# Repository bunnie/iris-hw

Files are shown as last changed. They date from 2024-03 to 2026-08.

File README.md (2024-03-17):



# IRIS CAD files

This repository contains IRIS CAD files not found elsewhere.

In particular, the base machine is the [Jubilee3D](https://jubilee3d.com/index.php?title=Main_Page); please refer to its [github](https://github.com/machineagency/jubilee) for its base CAD files.

## About IRIS

This repository is part of the IRIS project, an effort to make it easier to verify the construction of silicon chips.

Read more about IRIS at our [arXiv paper](https://arxiv.org/abs/2303.07406), or the latest [project update](https://www.bunniestudios.com/blog/?p=6937).

## Acknowledgements

This work was funded in part by NLnet’s [NGI0 Entrust](https://nlnet.nl/entrust/) fund, established with support from the European Commission’s Next Generation Internet Program, and my [Github Sponsors](https://github.com/sponsors/bunnie/).

NLnet Logo

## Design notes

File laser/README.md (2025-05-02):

# Laser Mount

This is an experimental extension to the IRIS tool that adds a laser
to the illumination capabilities. The driver is designed to work with
a 1064nm Fabrey-Perot laser diode with a max power rating of 300mW,
such as the ThorLabs L1064H1.

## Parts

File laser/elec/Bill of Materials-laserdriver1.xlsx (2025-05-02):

Comment | Description | Designator | Footprint | LibRef | Quantity | MPN | VENDOR
22uF, 6.3V, X5R | Capacitor (Semiconductor SIM Model) | C1 | B_CAP0603 | Cap Semi | 1 | CL10A226KQ8NRNE | Samsung
10uF, 6.3V, X5R | Capacitor (Semiconductor SIM Model) | C2, C4, C5, C6 | B_CAP0603 | Cap Semi | 4 | CL10A106MQ8NNNC | Samsung
0.1uF, 25V, X7R | Capacitor (Semiconductor SIM Model) | C3 | B_CAP0402 | Cap Semi | 1 | CL05A104KA5NNNC | Samsung
L1064H1 | Typical RED, GREEN, YELLOW, AMBER GaAs LED | D1 | TO-CAN-MICROJACK | LED2 | 1 | L1064H1 | Thorlabs
white LED | Typical RED, GREEN, YELLOW, AMBER GaAs LED | D2 | B_LED0805 | LED2 | 1 | EAST2012WA1 | Everlight
red LED | Typical RED, GREEN, YELLOW, AMBER GaAs LED | D3 | B_LED0805 | LED2 | 1 | ANY | ANY
USB4085-GF-A_REVB | USB-C (USB TYPE-C) USB 2.0 Receptacle Connector 24 (16+8 Dummy) Position Through Hole, Right Angle, low cost, 3.46mm profile, 16 pin, horizontal, Top mount | J1 | GCT_USB4085-GF-A_REVB | USB4085-GF-A_REVB | 1 | USB4085-GF-A | GCT
2.2uH SRP3212-2R2M | Magnetic-Core Inductor | L1 | B_IND1210_BOURNES | Inductor Iron | 1 | SRP3212-2R2M | Bournes
0.47uH 0603 | Magnetic-Core Inductor | L2 | B_IND0603 | Inductor Iron | 1 | TFM160808ALC-R47MTAA | TDK
917-43-103-41-005000 | Placeholder for non-board BOM items | NT1 |  | NOTE | 1 | 917-43-103-41-005000 | Mil-Max
FH34SRJ-10S-0.5SH | Header, 10-Pin | P1, P2 | HRS_FH34SRJ-10S-0.5SH(50) | Header 10 | 2 | FH34SRJ-10S-0.5SH | Hirose
Header 6 | Header, 6-Pin | P3 | HDR1X6 | Header 6 | 1
DMG1012UW-7 | N-Channel MOSFET | Q1, Q2 | SOT323-3AN | MOSFET-N | 2 | DMG1012UW-7 | Diodes Inc
10k, 1% | Resistor | R1, R2 | B_RES0402 | Res1 | 2 | ANY | ANY
0.33 ohm 1% | Resistor | R3 | B_RES0603 | Res1 | 1 | ERJ-3BQFR33V | Panasonic
3.3k, 1% | Resistor | R4, R5 | B_RES0402 | Res1 | 2 | ANY | ANY
0 ohm | Resistor | R6 | B_RES0402 | Res1 | 1 | ANY | ANY
51, 1% | Resistor | R7 | B_RES0603 | Res1 | 1 | ANY | ANY
180, 1% | Resistor | R8 | B_RES0603 | Res1 | 1 | ANY | ANY
249k, 1%, +/-200ppm | Resistor | R9 | B_RES0402 | Res1 | 1 | RC0402FR-07249KL | Yageo
5.1k, 1% | Resistor | R10, R11 | B_RES0603 | Res1 | 2 | RC0603FR-075K1L | Yageo
TPS92001 | 1.5A high efficiency synchronous buck LED driver | U1 | TI-WSON65P200X80_HS-7N | TPS92201 | 1
TMP1075NDRLR | Temperature sensor, I2C | U2 | TI-SON50P200X80_HS-9N | TMP1075N | 1
TPS62802 | Buck regulator, 4MHz, 0.6A, 1.8V-3.3V, low Iq | U3 | BGA6C35P2X3_70X105X40_NSMD | TPS62802 | 1 | TPS62802YKAR | TI

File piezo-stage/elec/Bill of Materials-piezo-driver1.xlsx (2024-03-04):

Comment | Description | Designator | Footprint | LibRef | Quantity | VENDOR | MPN
0.1uF, 25V, X7R | Capacitor (Semiconductor SIM Model) | C1, C2, C3, C4, C5, C6, C9, C10, C12, C13, C15, C19, C20, C30_D1, C30_D2, C30_D3, C31_D1, C31_D2, C31_D3 | B_CAP0603 | Cap Semi | 19 | Murata | CC0603KRX7R8BB104
2.2uF, 16V, X5R | Capacitor (Semiconductor SIM Model) | C7, C8, C11, C14, C25 | B_CAP0603 | Cap Semi | 5 | Samsung | CL10A225KO8NNNC
DNP | Capacitor (Semiconductor SIM Model) | C16 | B_CAP0603 | Cap Semi | 1 | DNP | DNP
15pF, 50V, NP0 | Capacitor (Semiconductor SIM Model) | C17, C18 | B_CAP0603 | Cap Semi | 2 | Samsung | CL10C150JB81PNC
10uF, 6.3V, X5R | Capacitor (Semiconductor SIM Model) | C21, C26, C27 | B_CAP0603 | Cap Semi | 3 | Samsung | CL10A106MQ8NNNC
10uF, 25V, X5R | Capacitor (Semiconductor SIM Model) | C22, C23, C28_D1, C28_D2, C28_D3 | B_CAP0805 | Cap Semi | 5 | Murata | GRM21BR61E106KA73L
0.033uF, 50V, X7R | Capacitor (Semiconductor SIM Model) | C24 | B_CAP0603 | Cap Semi | 1 | Samsung | CL10B333KB8NNNC
0.22uF, 250V X7R | Capacitor (Semiconductor SIM Model) | C29_D1, C29_D2, C29_D3 | B_CAP1210 | Cap Semi | 3 | Murata | GCJ32DR72E224KXJ1L
white LED | Typical RED, GREEN, YELLOW, AMBER GaAs LED | D1, D2 | B_LED0805 | LED2 | 2 | Everlight | EAST2012WA1
BZX38450-C1V8F | Schottky Diode | D3_D1, D3_D2, D3_D3 | SOD-323 | D Schottky | 3 | Nexperia | BZX38450-C1V8F
CDBA2200-HF | Schottky Diode | D4_D1, D4_D2, D4_D3 | DSO-C2/X1.8 | D Schottky | 3 | Comchip | CDBA2200-HF
USB4085-GF-A_REVB | USB-C (USB TYPE-C) USB 2.0 Receptacle Connector 24 (16+8 Dummy) Position Through Hole, Right Angle, low cost, 3.46mm profile, 16 pin, horizontal, Top mount | J1 | GCT_USB4085-GF-A_REVB | USB4085-GF-A_REVB | 1 | GCT | USB4085-GF-A
power tap (DNP) | Connector | J2 | RESTAP-0603 | CON1 | 1 | DNP | DNP
0.47uH 0603 | Magnetic-Core Inductor | L1 | B_IND0603 | Inductor Iron | 1 | TDK | TFM160808ALC-R47MTAA
3.3uH SRP3212A-3R3M | Magnetic-Core Inductor | L2_D1, L2_D2, L2_D3 | B_IND1210_BOURNES | Inductor Iron | 3 | Bournes | SRP3212A-3R3M
TTL-232R-3V3 | Placeholder for non-board BOM items | NT1 |  | NOTE | 1 | FTDI | TTL-232R-3V3
Header 4 | Header, 4-Pin | P1 | HDR1X4 | Header 4 | 1 | Adam Tech / ANY | PH1-04-UA / ANY
Male 2.54mm 6x1 header | Header, 6-Pin | P2 | HDR1X6 | Header 6 | 1 | Adam Tech / ANY | PH1-06-UA / ANY
2060-472/998-404 | Header, 2-Pin | P3_D1, P3_D2, P3_D3 | WAGO_2060-472/998-404 | Header 2 | 3 | WAGO | 2060-472/998-404
6mm square tact | Header, 2-Pin | PL1, PL2 | PANASONIC_EVPAS | Header 2 | 2 | Panasonic | EVP-ASAC1A
10k, 1% | Resistor | R1, R3, R5, R16_D1, R16_D2, R16_D3, R17_D1, R17_D2, R17_D3, R19_D1, R19_D2, R19_D3, R20_D1, R20_D2, R20_D3 | B_RES0603 | Res1 | 15 | Yageo | RC0603FR-0710KL
1k, 1% | Resistor | R2, R4, R13, R14 | B_RES0603 | Res1 | 4 | ANY | ANY
27, 1% | Resistor | R6, R7 | B_RES0603 | Res1 | 2 | ANY | ANY
5.1k, 1% | Resistor | R8 | B_RES0603 | Res1 | 1 | Yageo | RC0603FR-075K1L
DNP | Resistor | R9 | B_RES0603 | Res1 | 1 | DNP | DNP
51, 1% | Resistor | R10, R12 | B_RES0603 | Res1 | 2 | ANY | ANY
100k, 1% | Resistor | R11 | B_RES0603 | Res1 | 1 | Yageo | RC0603FR-07100KL
249k, 1%, +/-200ppm | Resistor | R15 | B_RES0402 | Res1 | 1 | Yageo | RC0402FR-07249KL
820k, 1% | Resistor | R18_D1, R18_D2, R18_D3 | B_RES0603 | Res1 | 3 | Yageo | RC0603FR-07820KL
100, 1% | Resistor | R21_D1, R21_D2, R21_D3 | B_RES0603 | Res1 | 3 | ANY | ANY
SN74AUP1T97DBVR | Low power configurable gate with voltage translator | U1 | SOT26A-6N | 74AUP1T97L6X | 1 | TI | SN74AUP1T97DBVR
RP2040 | RP2040 chip for Raspberry Pi Pico - ARMÂ® CortexÂ®-M0+ MCU 32-Bit | U2 | QFN40P700X700X90-57N | RP2040 | 1 | Raspberry Pi | SC0914(7/13)
DAC70504 | Quad SPI DAC with internal reference, in 16- (8), 14- (7), and 12-(6) bit variants | U3 | QFN50P300X300X80_HS-17N | DACx0504 | 1 | TI | DAC70504RTET
W25Q16JVSSIQ | 16Mbit SPI NOR FLASH | U4 | SOIC127P790X216-8N | EN25P05-50GCP | 1 | Winbond | W25Q16JVSSIQ
LP3982IMM-3.3/NOPB | Micropower, Ultra Low-Dropout, Low-Noise, 300mA CMOS Regulator, 8-pin Mini SOIC, Pb-Free | U5 | MUA08A_N | LP3982IMM-3.3/NOPB | 1 | TI | LP3982IMM-3.3/NOPB
ER-OLEDM0.66-1W-I2C | 0.66" white OLED module, I2C | U6 | ER-OLEDM0.66-1W-I2C | ER-OLEDM0.66-1W-I2C | 1 | East Rising | ER-OLEDM0.66-1W-I2C
TPS62802 | Buck regulator, 4MHz, 0.6A, 1.8V-3.3V, low Iq | U7 | BGA6C35P2X3_70X105X40_NSMD | TPS62802 | 1 | TI | TPS62802YKAR
DRV2700RGPR | Motor Driver Analog 20-QFN _4x4_ | U8_D1, U8_D2, U8_D3 | QFN50P400X400X100_HS-21N_DRV2700 | DRV2700RGPR | 3 | TI | DRV2700RGP(T/R)
12.0000 MHz 12pF | Crystal Oscillator | Y1 | NDK_NX5032A | XTAL | 1 | ECS | ECS-120-12-30-JGN-TR

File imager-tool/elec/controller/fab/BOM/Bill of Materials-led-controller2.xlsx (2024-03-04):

Comment | Description | Designator | Footprint | LibRef | Quantity | VENDOR | MPN
0.1uF, 25V, X7R | Capacitor (Semiconductor SIM Model) | C1, C2, C3, C4, C5, C6, C9, C12, C13, C15 | B_CAP0603 | Cap Semi | 10 | Murata | CC0603KRX7R8BB104
2.2uF, 16V, X5R | Capacitor (Semiconductor SIM Model) | C7, C8, C11, C14 | B_CAP0603 | Cap Semi | 4 | Samsung | CL10A225KO8NNNC
22uF, 50V | Polarized Capacitor (Radial) | C10 | CAPAE7066X61N | Cap Pol1 | 1 | Panasonic | EEH-ZA1H220P
15pF, 50V, NP0 | Capacitor (Semiconductor SIM Model) | C17, C18 | B_CAP0603 | Cap Semi | 2 | Samsung | CL10C150JB81PNC
10uF, 6.3V, X5R | Capacitor (Semiconductor SIM Model) | C21, C26, C27 | B_CAP0603 | Cap Semi | 3 | Samsung | CL10A106MQ8NNNC
white LED | Typical RED, GREEN, YELLOW, AMBER GaAs LED | D1 | B_LED0805 | LED2 | 1 | Everlight | EAST2012WA1
USB4085-GF-A_REVB | USB-C (USB TYPE-C) USB 2.0 Receptacle Connector 24 (16+8 Dummy) Position Through Hole, Right Angle, low cost, 3.46mm profile, 16 pin, horizontal, Top mount | J1 | GCT_USB4085-GF-A_REVB | USB4085-GF-A_REVB | 1 | GCT | USB4085-GF-A
0.47uH 0603 | Magnetic-Core Inductor | L1 | B_IND0603 | Inductor Iron | 1 | TDK | TFM160808ALC-R47MTAA
FPC cable, 4" | Placeholder for non-board BOM items | NT1, NT2 |  | NOTE | 2 | assmann WSW Components | AFFC-050-06-102-11
TTL-232R-3V3 | Placeholder for non-board BOM items | NT3 |  | NOTE | 1 | FTDI | TTL-232R-3V3
Header 4 | Header, 4-Pin | P1 | HDR1X4 | Header 4 | 1 | Adam Tech / ANY | PH1-04-UA / ANY
Male 2.54mm 6x1 header | Header, 6-Pin | P2 | HDR1X6 | Header 6 | 1 | Adam Tech / ANY | PH1-06-UA / ANY
FH34SRJ-6S-0.5SH(50) | Header, 6-Pin | P3, P4, P5, P6, P7 | HRS_FH34SRJ-6S-0.5SH(50) | Header 6 | 5 | HRS | FH34SRJ-6S-0.5SH(50)
Mini Tact | Header, 2-Pin | PL1, PL2 | OMRON_B3U-1000P | Header 2 | 2 | Omron | B3U-1000P
10k, 1% | Resistor | R1, R3, R9, R11, R12, R13 | B_RES0603 | Res1 | 6 | Yageo | RC0603FR-0710KL
1k, 1% | Resistor | R2, R4 | B_RES0603 | Res1 | 2 | ANY | ANY
27, 1% | Resistor | R5, R6, R7, R18 | B_RES0603 | Res1 | 4 | ANY | ANY
5.1k, 1% | Resistor | R8, R19 | B_RES0603 | Res1 | 2 | Yageo | RC0603FR-075K1L
51, 1% | Resistor | R10 | B_RES0603 | Res1 | 1 | ANY | ANY
249k, 1%, +/-200ppm | Resistor | R15 | B_RES0402 | Res1 | 1 | Yageo | RC0402FR-07249KL
OKI-78SR-5/1.5-W36-C | OKI-78SR switching regulator | U1 | MURATA_OKI-78SR | VR20 | 1 |  | OKI-78SR-5/1.5-W36-C
RP2040 | RP2040 chip for Raspberry Pi Pico - ARMÂ® CortexÂ®-M0+ MCU 32-Bit | U2 | QFN40P700X700X90-57N | RP2040 | 1 | Raspberry Pi | SC0914(7/13)
W25Q16JVUXIQ | 16Mbit SPI NOR FLASH | U4 | USON-8 | EN25P05-50GCP | 1 | Winbond | W25Q16JVUXIQ
TPS62802 | Buck regulator, 4MHz, 0.6A, 1.8V-3.3V, low Iq | U7 | BGA6C35P2X3_70X105X40_NSMD | TPS62802 | 1 | TI | TPS62802YKAR
12.0000 MHz 12pF | Crystal Oscillator | Y1 | NDK_NX5032A | XTAL | 1 | ECS | ECS-120-12-30-JGN-TR

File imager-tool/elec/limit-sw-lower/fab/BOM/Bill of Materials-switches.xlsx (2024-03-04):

Comment | Description | Designator | Footprint | LibRef | Quantity | MPN | MFG
FH34SRJ-6S-0.5SH(50) | Header, 6-Pin | P1, P2 | HRS_FH34SRJ-6S-0.5SH(50) | Header 6 | 2 | FH34SRJ-6S-0.5SH(50)
SW-SPST | Single-Pole, Single-Throw Switch | S1 | ESE22MH22 | SW-SPST | 1 | ESE22MH22 | Panasonic
SW-SPST | Single-Pole, Single-Throw Switch | S2 | ESE22MH24 | SW-SPST | 1 | ESE22MH24 | Panasonic

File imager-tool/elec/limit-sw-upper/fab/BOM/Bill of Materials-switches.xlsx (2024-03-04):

Comment | Description | Designator | Footprint | LibRef | Quantity | MPN | MFG
FH34SRJ-6S-0.5SH(50) | Header, 6-Pin | P3 | HRS_FH34SRJ-6S-0.5SH(50) | Header 6 | 1 | FH34SRJ-6S-0.5SH(50)
SW-SPST | Single-Pole, Single-Throw Switch | S2 | ESE22MH24 | SW-SPST | 1 | ESE22MH24 | Panasonic

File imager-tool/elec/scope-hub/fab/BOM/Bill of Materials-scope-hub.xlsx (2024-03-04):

Comment | Description | Designator | Footprint | LibRef | Quantity | VENDOR | MPN
TTL-232R-3V3 | Placeholder for non-board BOM items | NT1, NT2, NT3 |  | NOTE | 3 | FTDI | TTL-232R-3V3
26-pin FPC | 26 Pin FPC header | P1, P2 | HRS_FH34SRJ-26S-0.5SH(50) | FPC-26 | 2 | Hirose | FH34SRJ-26S-0.5SH(99)
Microfit vertical header | Header, 2-Pin | P3, P4 | MOLEX_0436500217 | Header 2 | 2 | Molex | 0436500217
Male 2.54mm 6x1 header | Header, 6-Pin | P5, P6, P7 | HDR1X6 | Header 6 | 3 | Adam Tech / ANY | PH1-06-UA / ANY
27, 1% | Resistor | R1, R2, R3, R4, R5, R6 | B_RES0603 | Res1 | 6 | ANY | ANY

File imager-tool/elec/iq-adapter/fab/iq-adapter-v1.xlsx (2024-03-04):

Comment | Description | Designator | Footprint | LibRef | Quantity | MPN | VENDOR
26-pin FPC | 26 Pin FPC header | P1, P2 | HRS_FH34SRJ-26S-0.5SH(50) | FPC-26 | 2 | FH34SRJ-26S-0.5SH(99) | Hirose
FH34SRJ-6S-0.5SH(50) | Header, 6-Pin | P3 | HRS_FH34SRJ-6S-0.5SH(50) | Header 6 | 1 | FH34SRJ-6S-0.5SH(50) | HRS

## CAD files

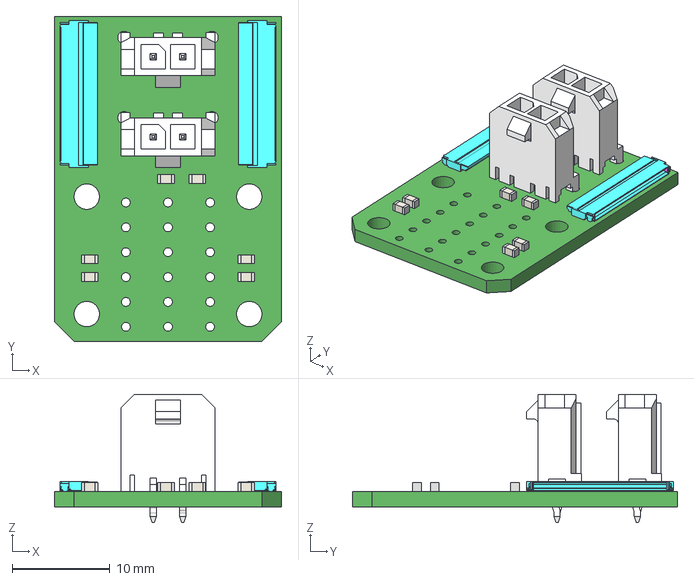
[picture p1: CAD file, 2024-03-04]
imager-tool/elec/scope-hub/fab/ExportSTEP/scope-hub.step
23.2 x 33.2 x 13.1 mm

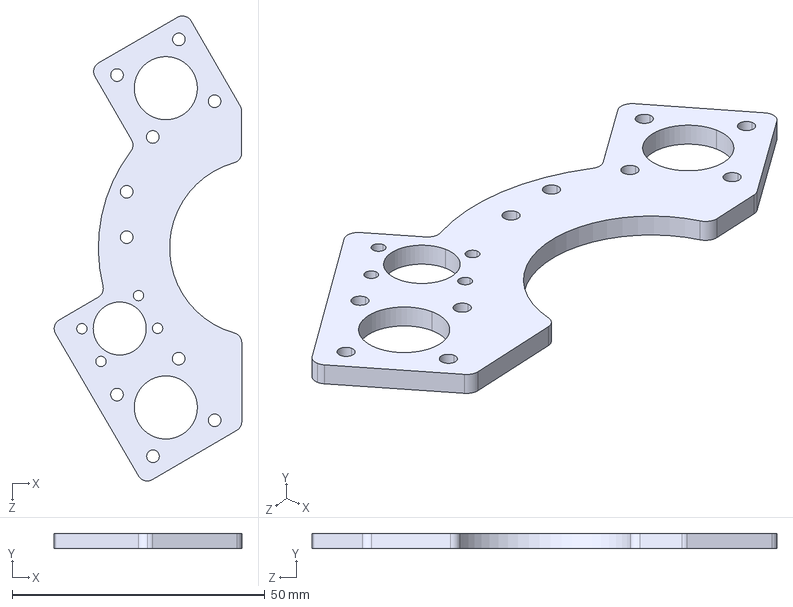
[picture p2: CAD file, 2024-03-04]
imager-tool/mech/iris-thustplate.STEP
37.1 x 3.00 x 92.1 mm

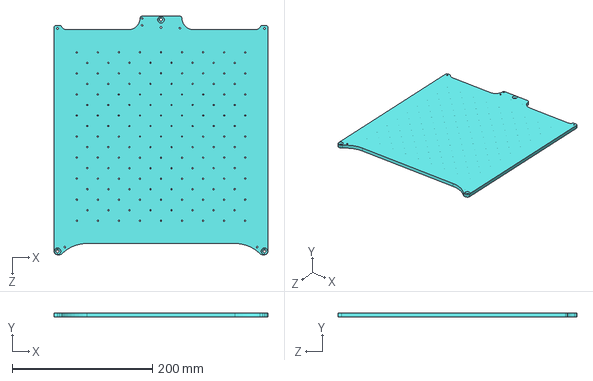
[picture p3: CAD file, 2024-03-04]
jubilee/z_plate_3.STEP
305.0 x 6.35 x 340.0 mm

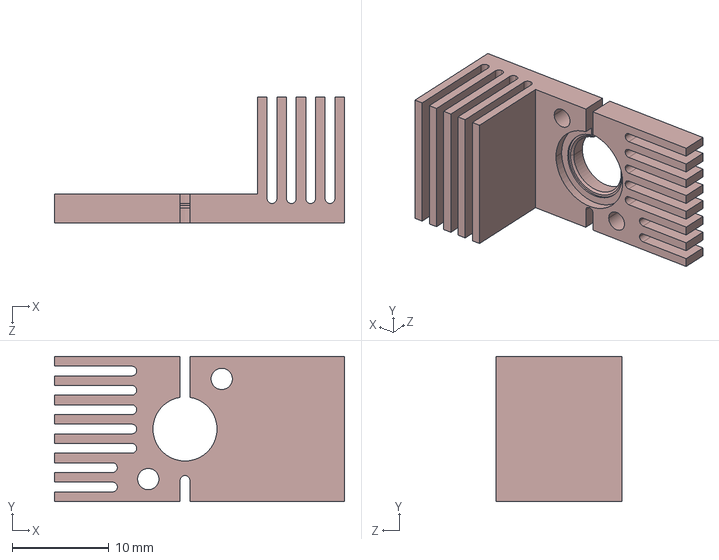
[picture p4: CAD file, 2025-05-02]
laser/mech/ld-hs.STEP
30.0 x 15.0 x 13.0 mm

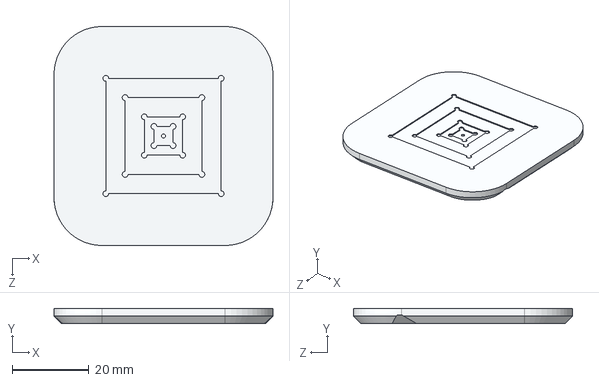
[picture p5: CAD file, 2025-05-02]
piezo-stage/mech/piezo-top-plate-square.STEP
57.0 x 4.00 x 57.0 mm

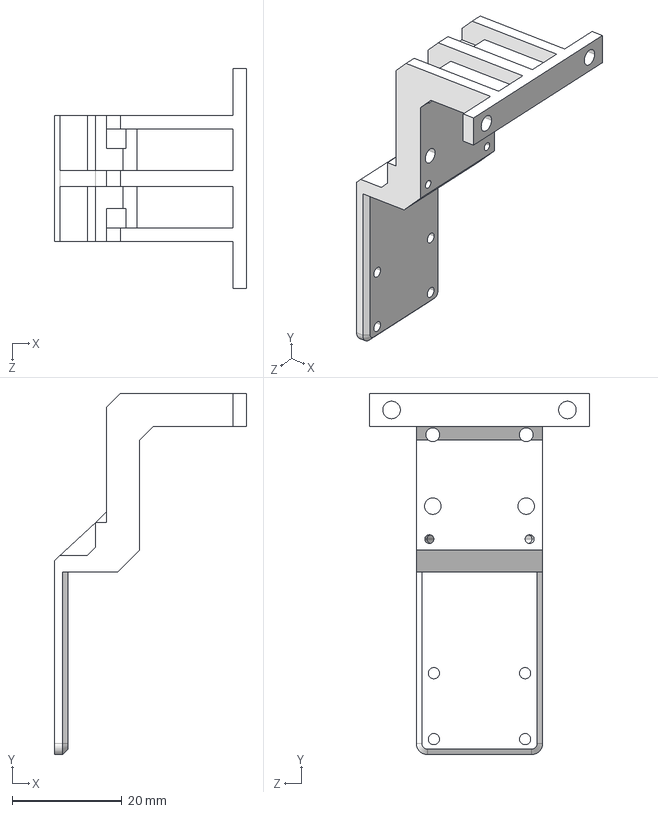
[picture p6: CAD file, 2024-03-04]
imager-tool/mech/iris-carriage-plate.STEP
35.0 x 65.7 x 40.0 mm

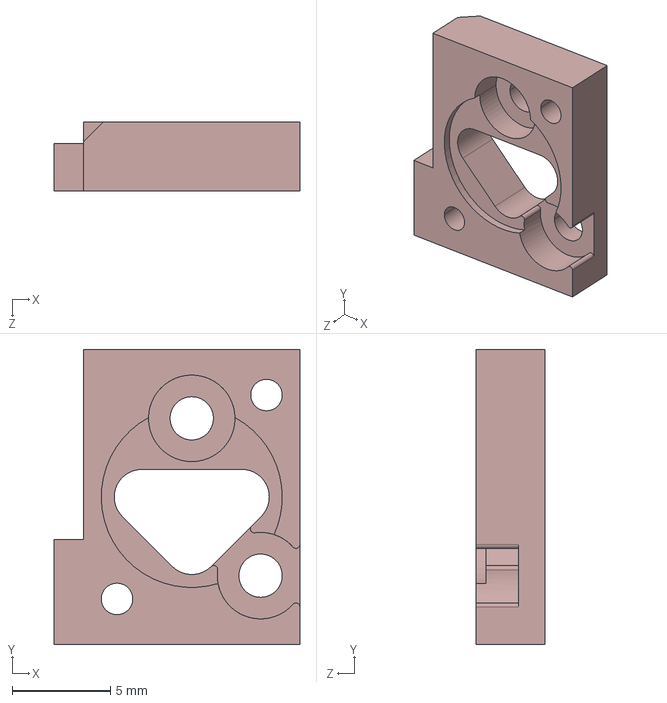
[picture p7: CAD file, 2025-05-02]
laser/mech/ld-hs-interposer.STEP
12.5 x 15.0 x 3.50 mm

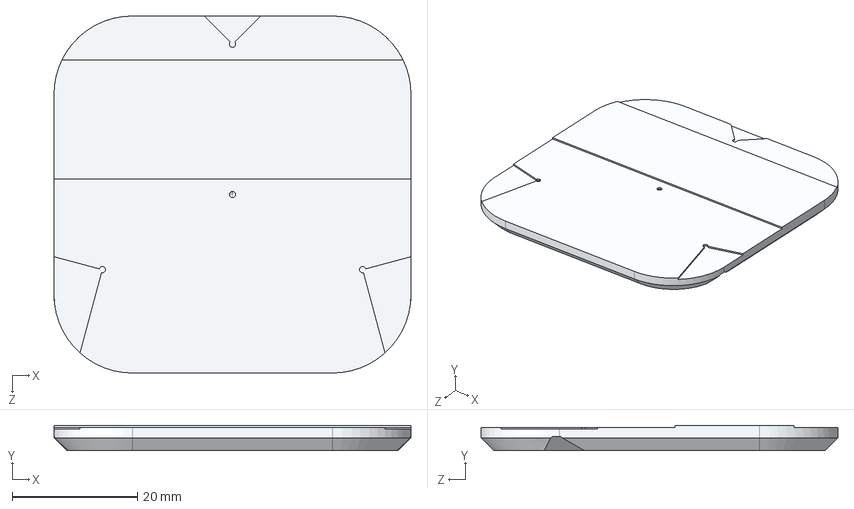
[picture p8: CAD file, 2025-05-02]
piezo-stage/mech/piezo-top-plate-square-1d.STEP
57.0 x 4.00 x 57.0 mm

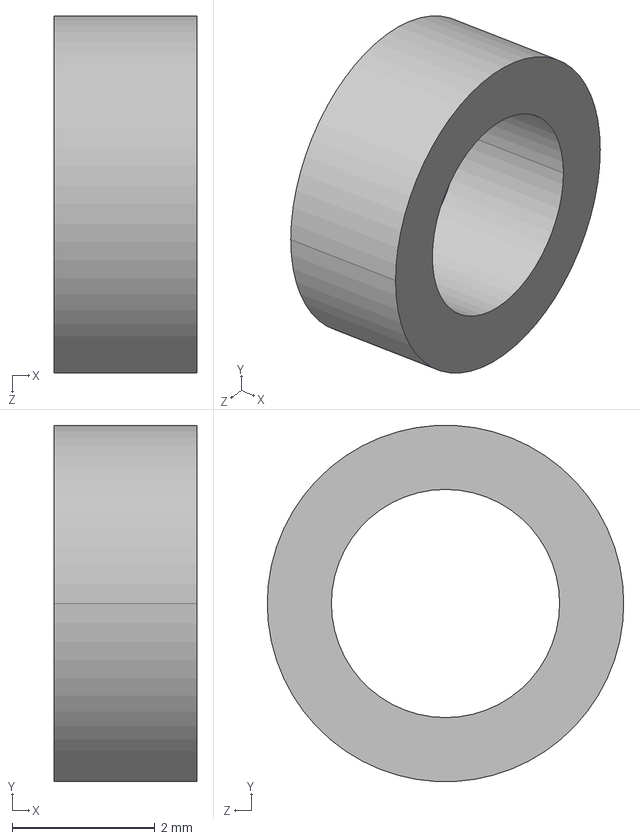
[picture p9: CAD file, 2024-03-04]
imager-tool/mech/iris-pom-spacer.STEP
2.00 x 4.99 x 5.00 mm

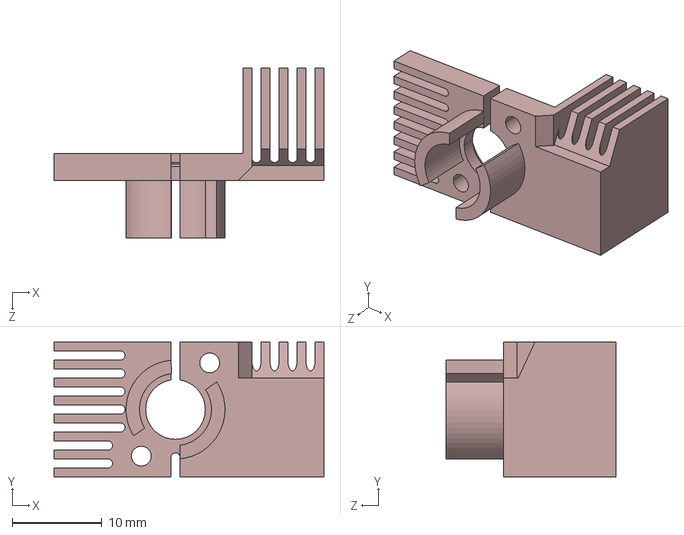
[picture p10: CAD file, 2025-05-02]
laser/mech/ld-hs-v2.STEP
30.0 x 15.0 x 18.9 mm

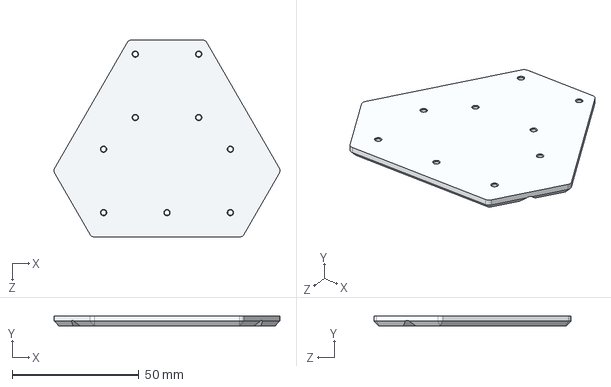
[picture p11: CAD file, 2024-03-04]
piezo-stage/mech/piezo-top-plate.STEP
89.1 x 4.00 x 77.7 mm

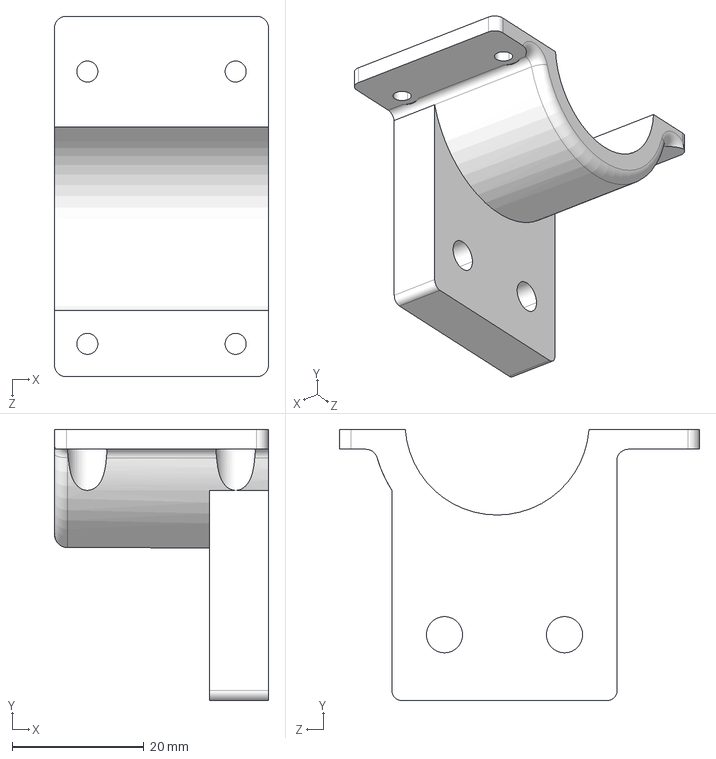
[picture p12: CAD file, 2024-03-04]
imager-tool/mech/iris-motor-clip.STEP
32.6 x 41.2 x 54.8 mm

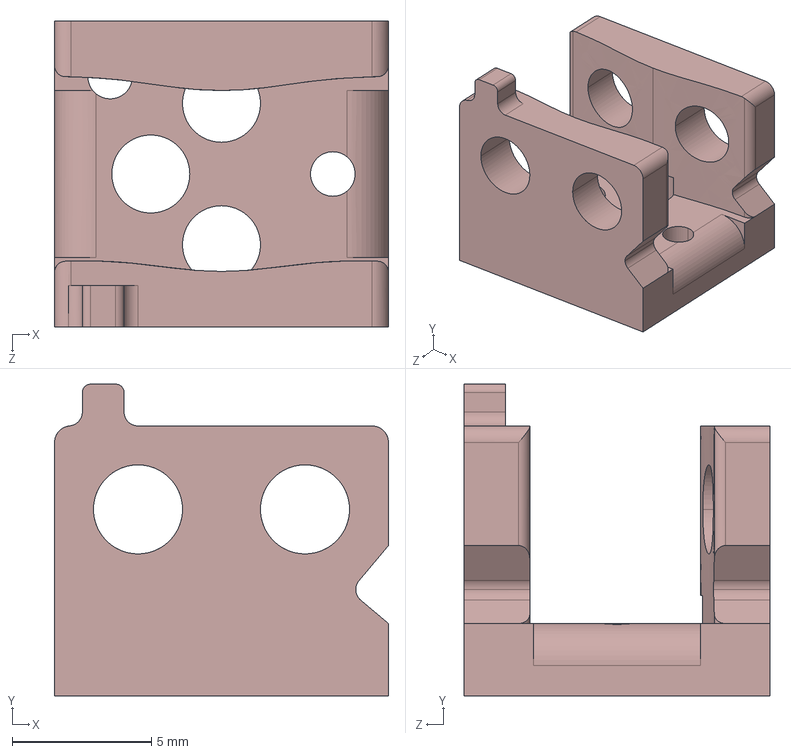
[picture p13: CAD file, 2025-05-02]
laser/mech/iris-lightshuttle-ld.STEP
12.0 x 11.2 x 11.0 mm

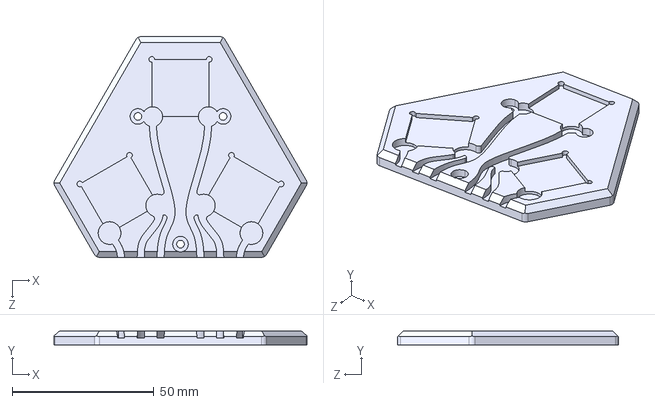
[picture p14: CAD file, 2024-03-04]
piezo-stage/mech/piezo-mounting-plate.STEP
89.1 x 5.00 x 77.7 mm

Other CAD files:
imager-tool/mech/iris-rel-mounting-plate.SLDPRT
laser/mech/laser-thrust-plate.STL
imager-tool/mech/iris-pulley-v2.STEP
laser/mech/hinge.STL
imager-tool/mech/IQ2306 6mm adapter v2.STEP
imager-tool/mech/iris-actuator-base-plate.SLDDRW
imager-tool/mech/iris-alignment-bracket.SLDDRW
imager-tool/mech/iris-alignment-bracket.SLDPRT
imager-tool/mech/iris-alignment-bracket.STEP
imager-tool/mech/iris-carriage-plate.SLDDRW
imager-tool/mech/iris-carriage-plate.SLDPRT
imager-tool/mech/iris-connecting-rod.SLDDRW
imager-tool/mech/iris-connecting-rod.SLDPRT
imager-tool/mech/iris-connecting-rod.STEP
imager-tool/mech/iris-coupling-plate-v2.SLDDRW
imager-tool/mech/iris-coupling-plate-v2.SLDPRT
imager-tool/mech/iris-coupling-plate-v2.STEP
imager-tool/mech/iris-drive-pulley.SLDDRW
imager-tool/mech/iris-drive-pulley.SLDPRT
imager-tool/mech/iris-drive-pulley.STEP
imager-tool/mech/iris-endplate.SLDDRW
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

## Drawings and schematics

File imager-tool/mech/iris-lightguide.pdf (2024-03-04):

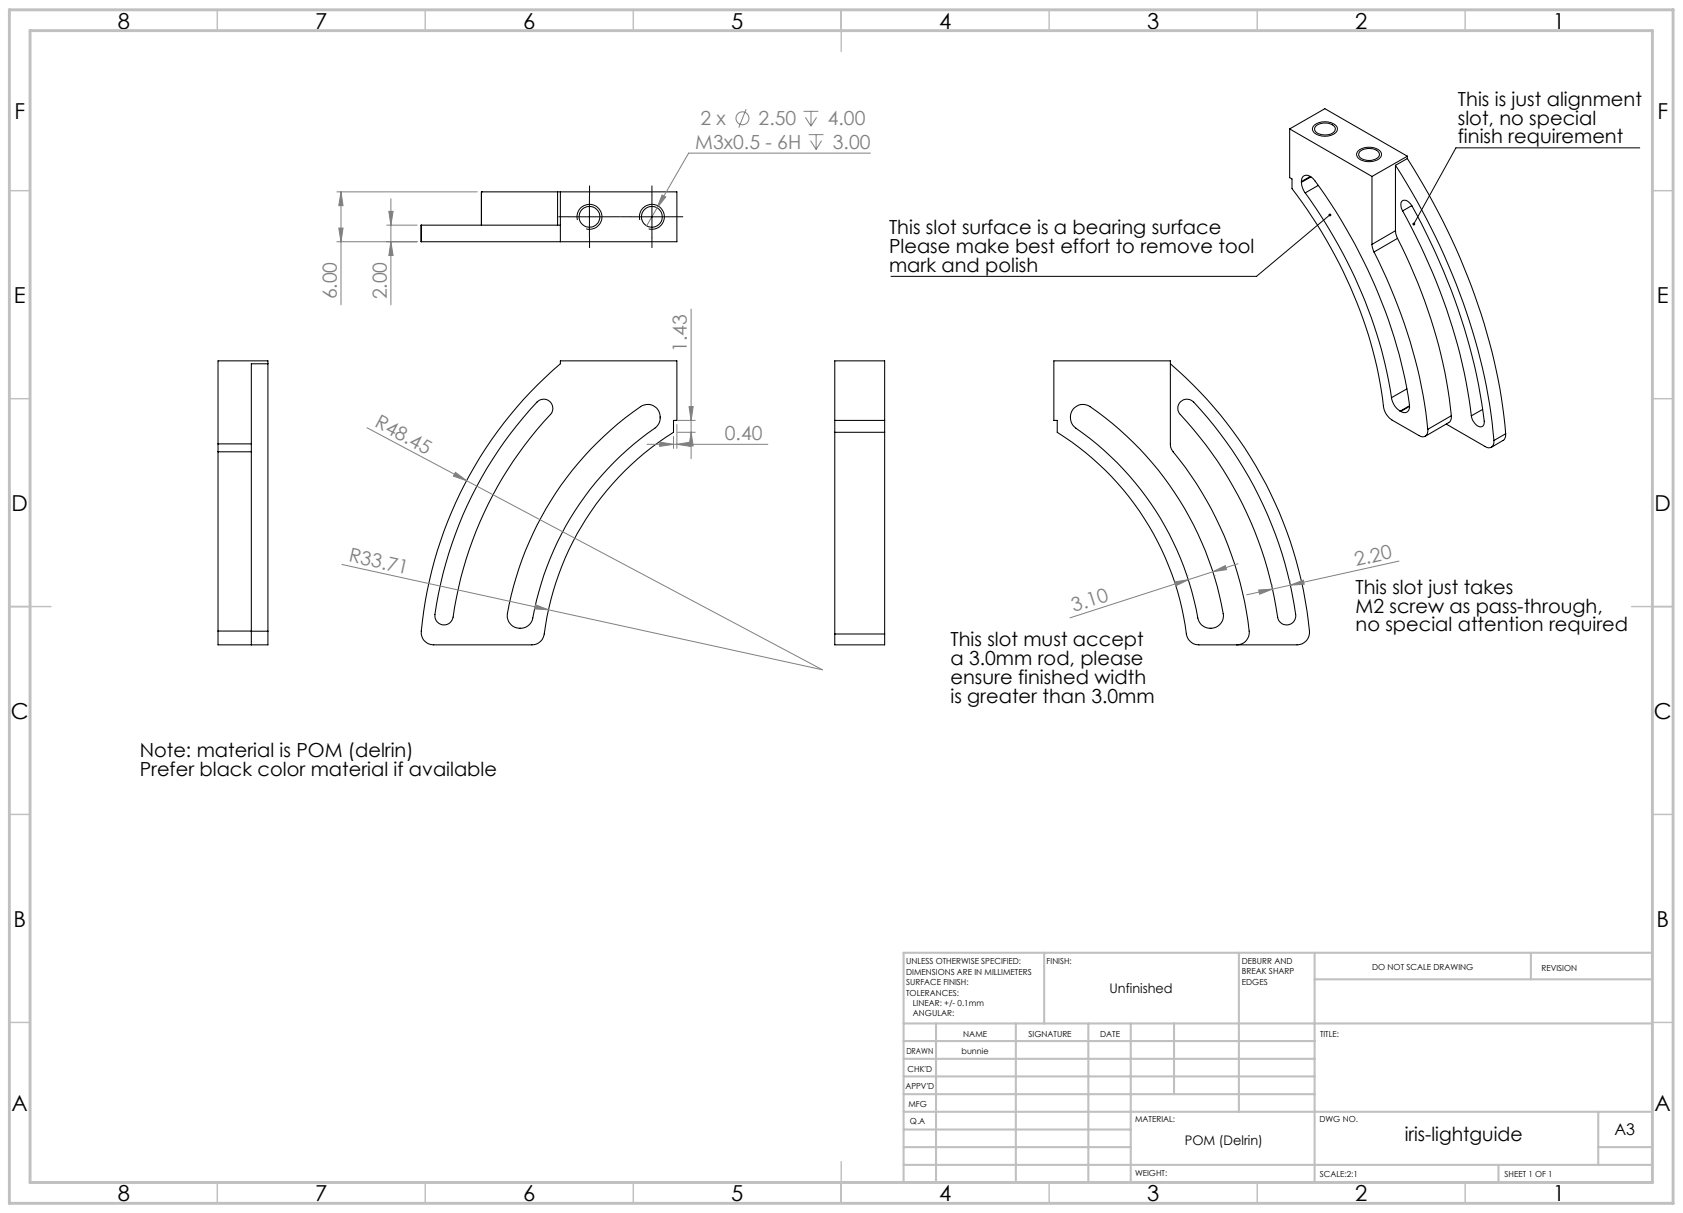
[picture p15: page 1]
FINISH:; DEBURR AND; BREAK SHARP; DO NOT SCALE DRAWING; REVISION; SCALE:2:1; SHEET 1 OF 1

This is just alignment
slot, no special
finish requirement

This slot surface is a bearing surface
Please make best effort to remove tool
mark and polish

This slot just takes
M2 screw as pass-through,
no special attention required

This slot must accept
a 3.0mm rod, please
ensure finished width
is greater than 3.0mm

Note: material is POM (delrin)
Prefer black color material if available

UNLESS OTHERWISE SPECIFIED:
DIMENSIONS ARE IN MILLIMETERS
SURFACE FINISH:
TOLERANCES:
LINEAR: +/- 0.1mm
ANGULAR:

NAME | SIGNATURE | DATE | | | | TITLE:

DRAWN | bunnie
CHK'D
APPV'D
MFG
Q.A | | | | MATERIAL: | DWG NO. iris-lightguide | A3 POM (Delrin)

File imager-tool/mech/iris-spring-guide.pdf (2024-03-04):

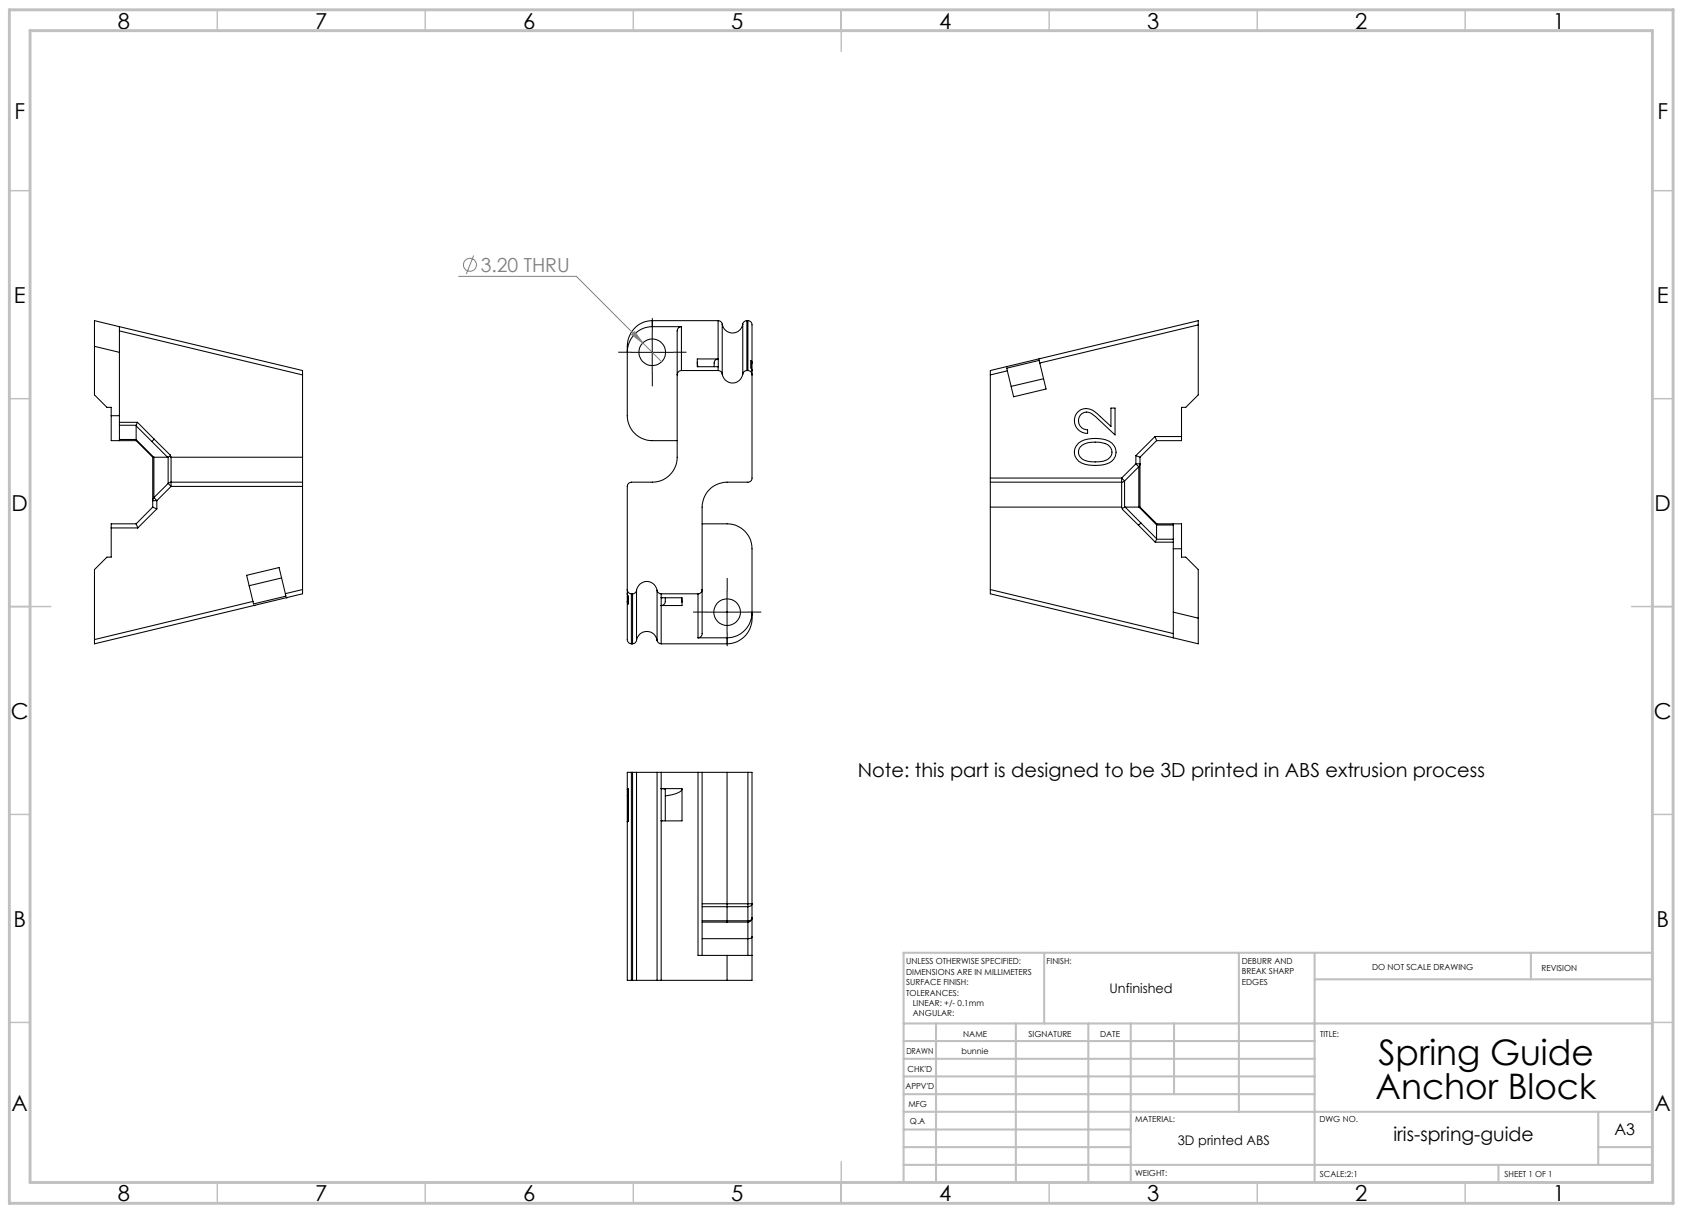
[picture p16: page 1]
3.20 THRU; FINISH:; DEBURR AND; BREAK SHARP; DO NOT SCALE DRAWING; REVISION; SCALE:2:1; SHEET 1 OF 1

Note: this part is designed to be 3D printed in ABS extrusion process

UNLESS OTHERWISE SPECIFIED:
DIMENSIONS ARE IN MILLIMETERS
SURFACE FINISH:
TOLERANCES:
LINEAR: +/- 0.1mm
ANGULAR:

NAME | SIGNATURE | DATE | | | | TITLE: Spring Guide Anchor Block

DRAWN | bunnie
CHK'D
APPV'D
MFG
Q.A | | | | MATERIAL: | DWG NO. iris-spring-guide | A3 3D printed ABS

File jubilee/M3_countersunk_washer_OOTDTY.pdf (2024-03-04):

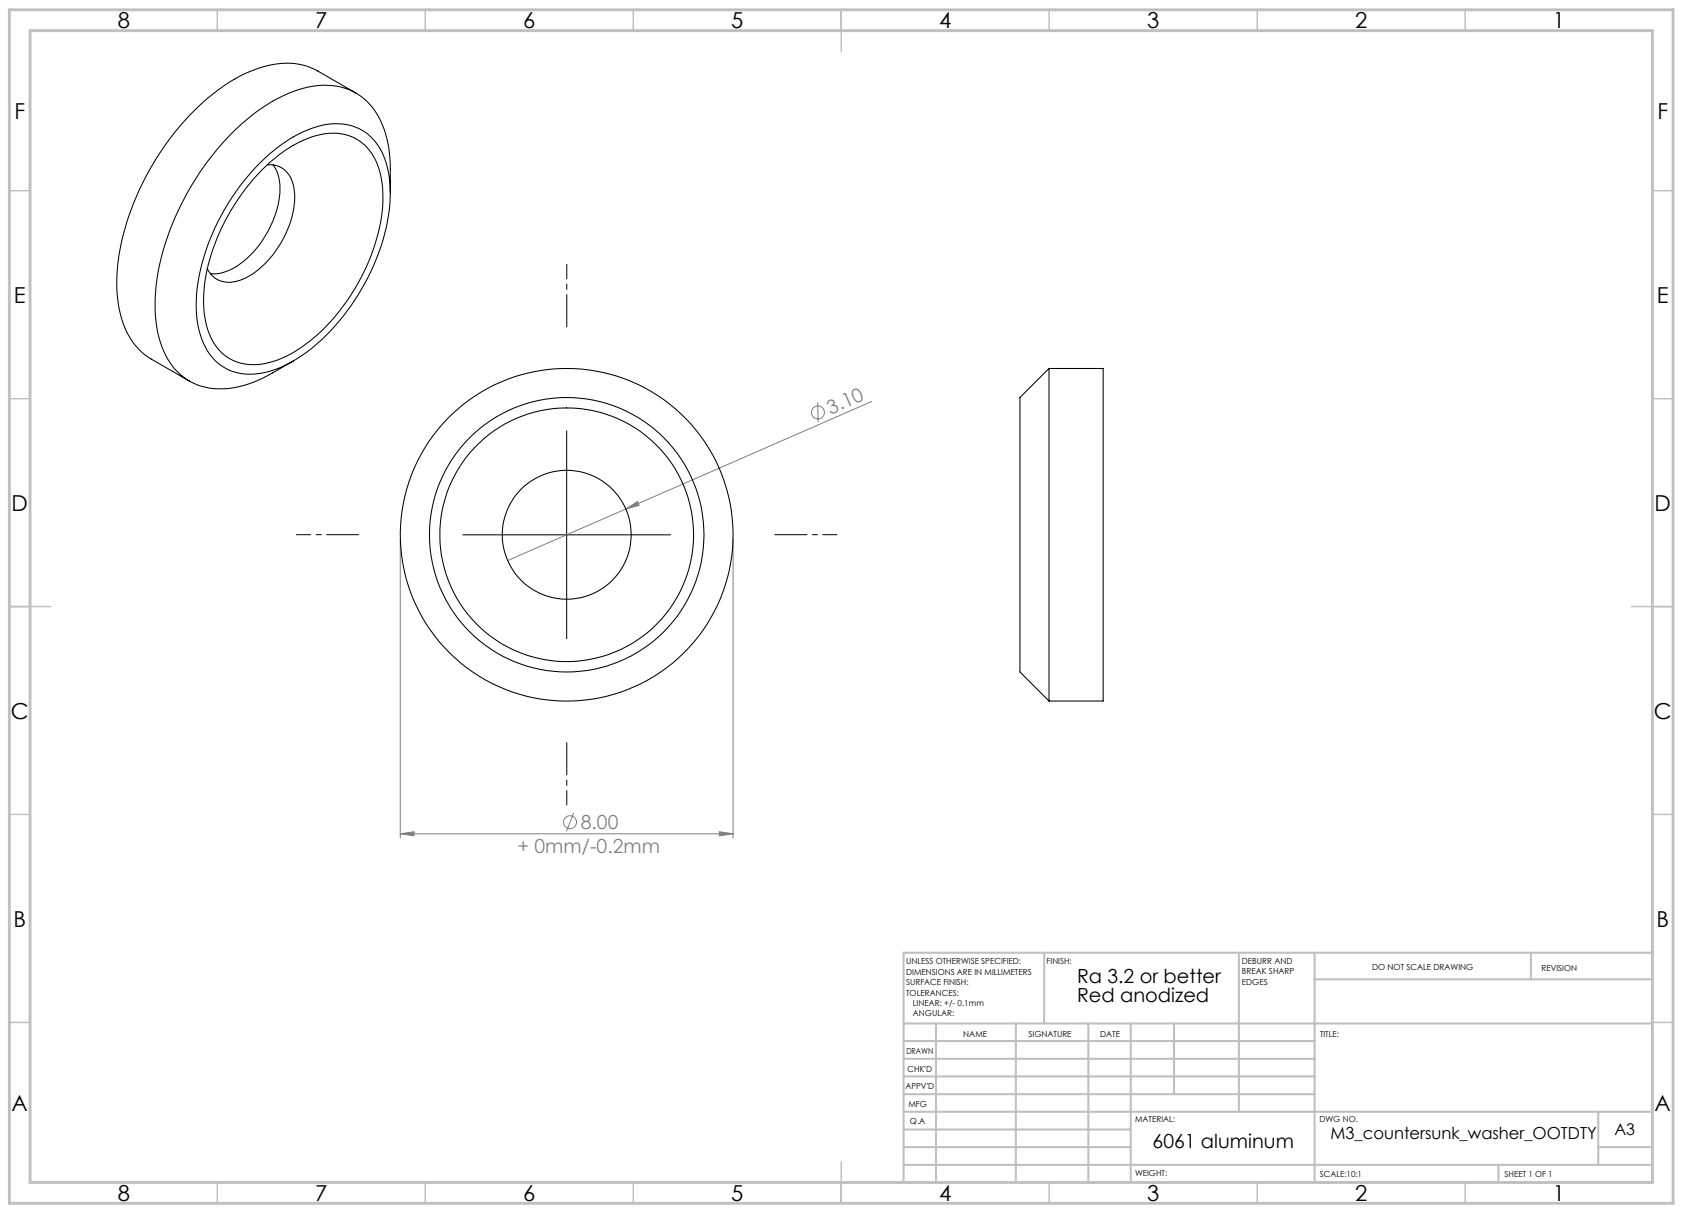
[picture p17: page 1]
FINISH:; DEBURR AND; BREAK SHARP; DO NOT SCALE DRAWING; REVISION; SCALE:10:1; SHEET 1 OF 1

UNLESS OTHERWISE SPECIFIED:
DIMENSIONS ARE IN MILLIMETERS
SURFACE FINISH:
TOLERANCES:
LINEAR: +/- 0.1mm
ANGULAR:

Ra 3.2 or better
Red anodized

NAME | SIGNATURE | DATE | | | | TITLE:

DRAWN
CHK'D
APPV'D
MFG
Q.A | | | | MATERIAL: 6061 aluminum | DWG NO. M3_countersunk_washer_OOTDTY | A3

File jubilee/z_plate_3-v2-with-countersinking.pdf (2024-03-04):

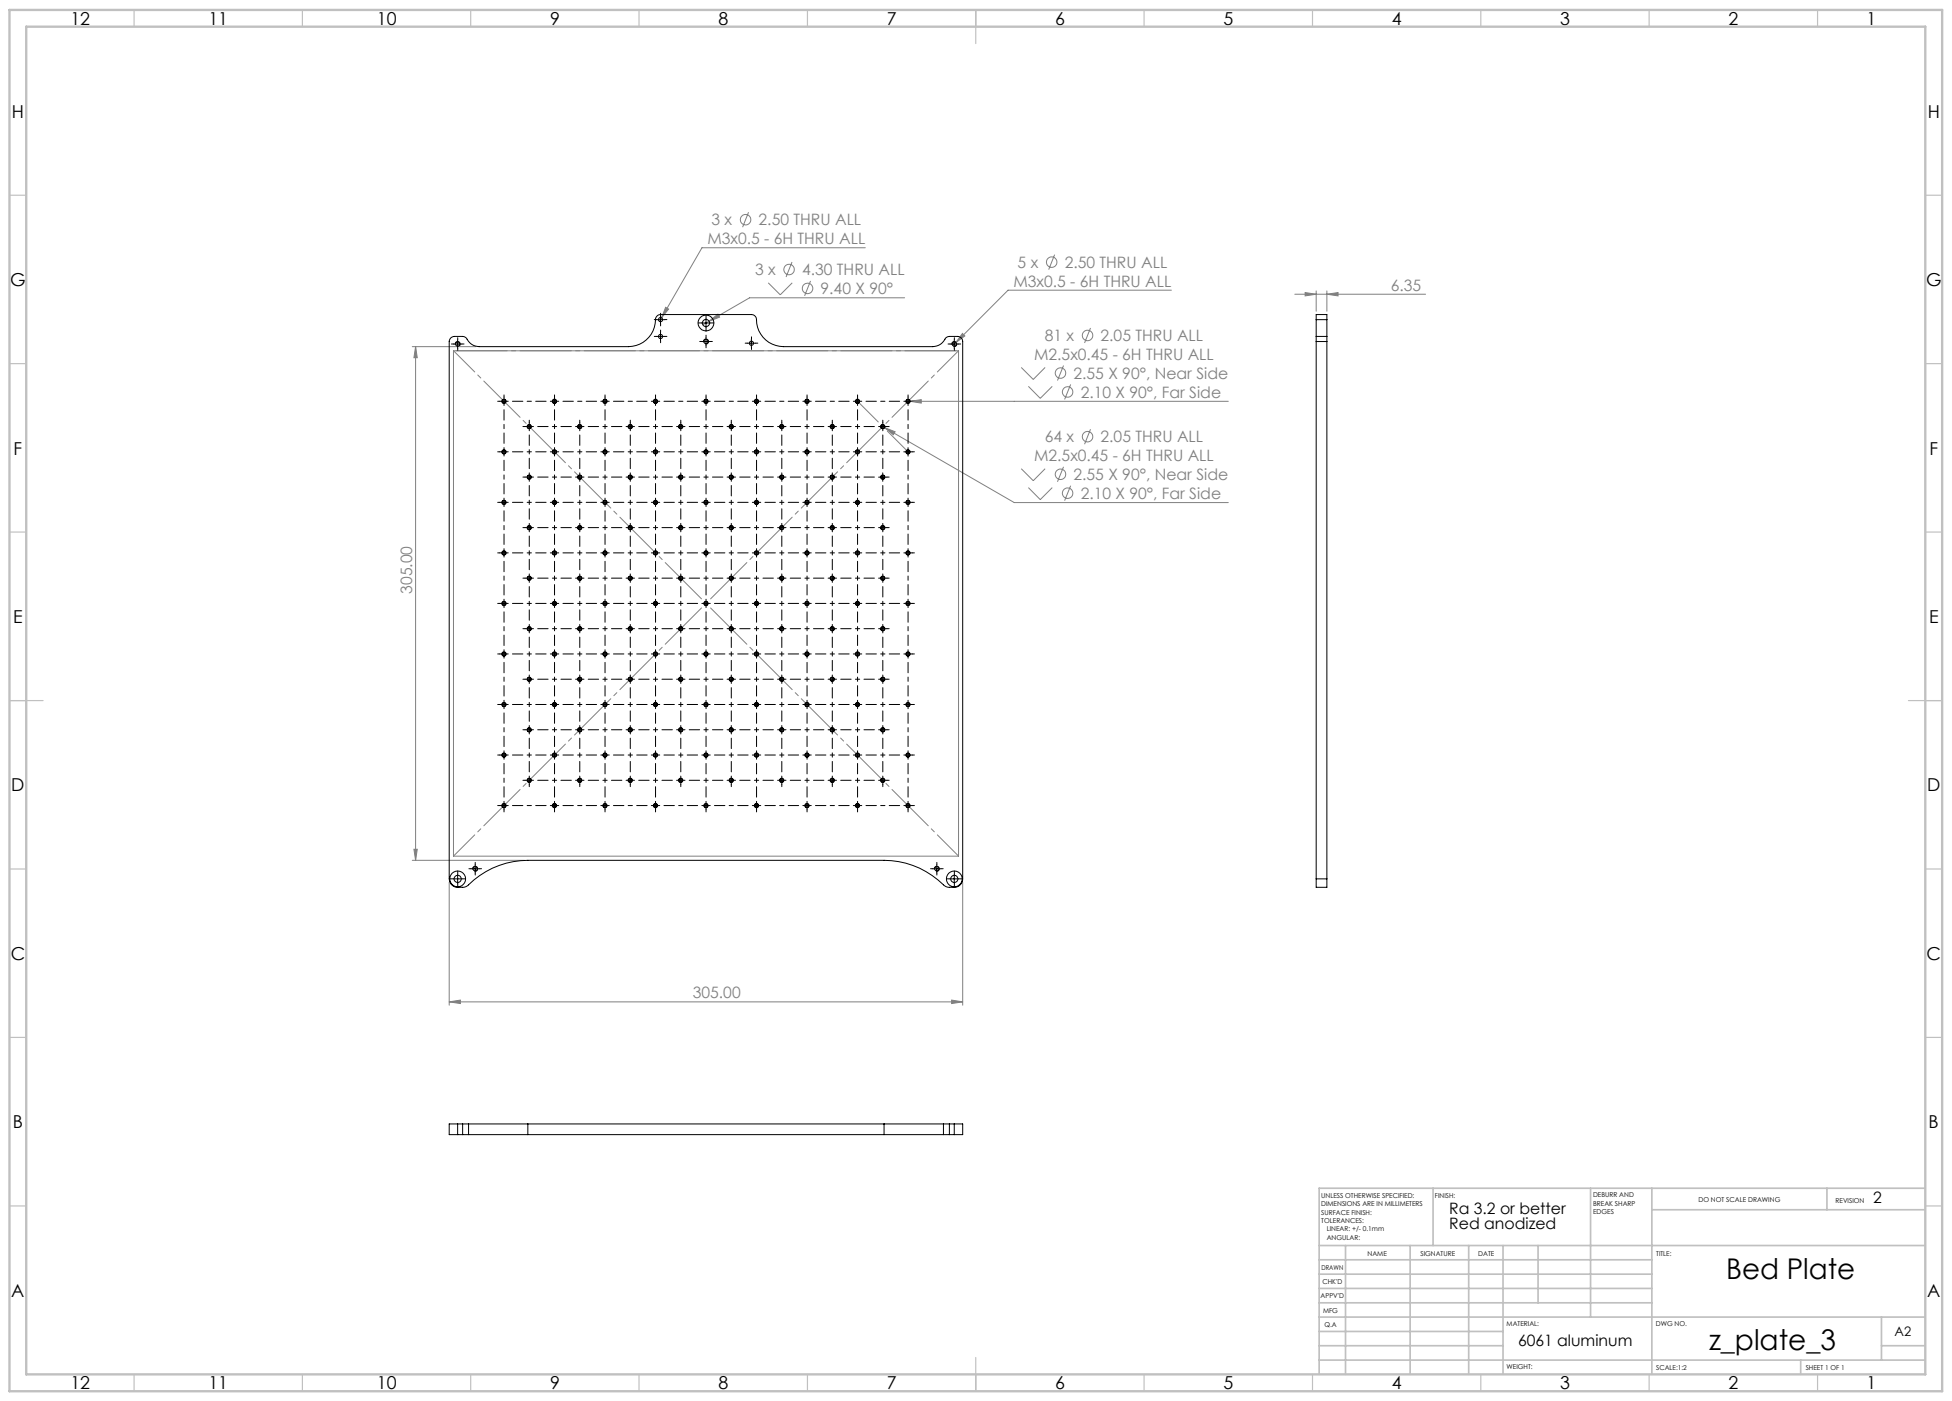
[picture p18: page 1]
2.05 THRU ALL; M2.5x0.45 - 6H THRU ALL 2.55 X 90°, Near Side 2.10 X 90°, Far Side; 2.50 THRU ALL; M3x0.5 - 6H THRU ALL; 4.30 THRU ALL; SCALE:1:2; SHEET 1 OF 1

UNLESS OTHERWISE SPECIFIED: DIMENSIONS ARE IN MILLIMETERS SURFACE FINISH: TOLERANCES: LINEAR: +/- 0.1mm ANGULAR: | FINISH: Ra 3.2 or better Red anodized | DEBURR AND BREAK SHARP EDGES | DO NOT SCALE DRAWING | 2 REVISION

NAME | SIGNATURE | DATE | | | | TITLE: Bed Plate

DRAWN
CHK'D
APPV'D
MFG
Q.A | | | | MATERIAL: 6061 aluminum | DWG NO. z_plate_3 | A2

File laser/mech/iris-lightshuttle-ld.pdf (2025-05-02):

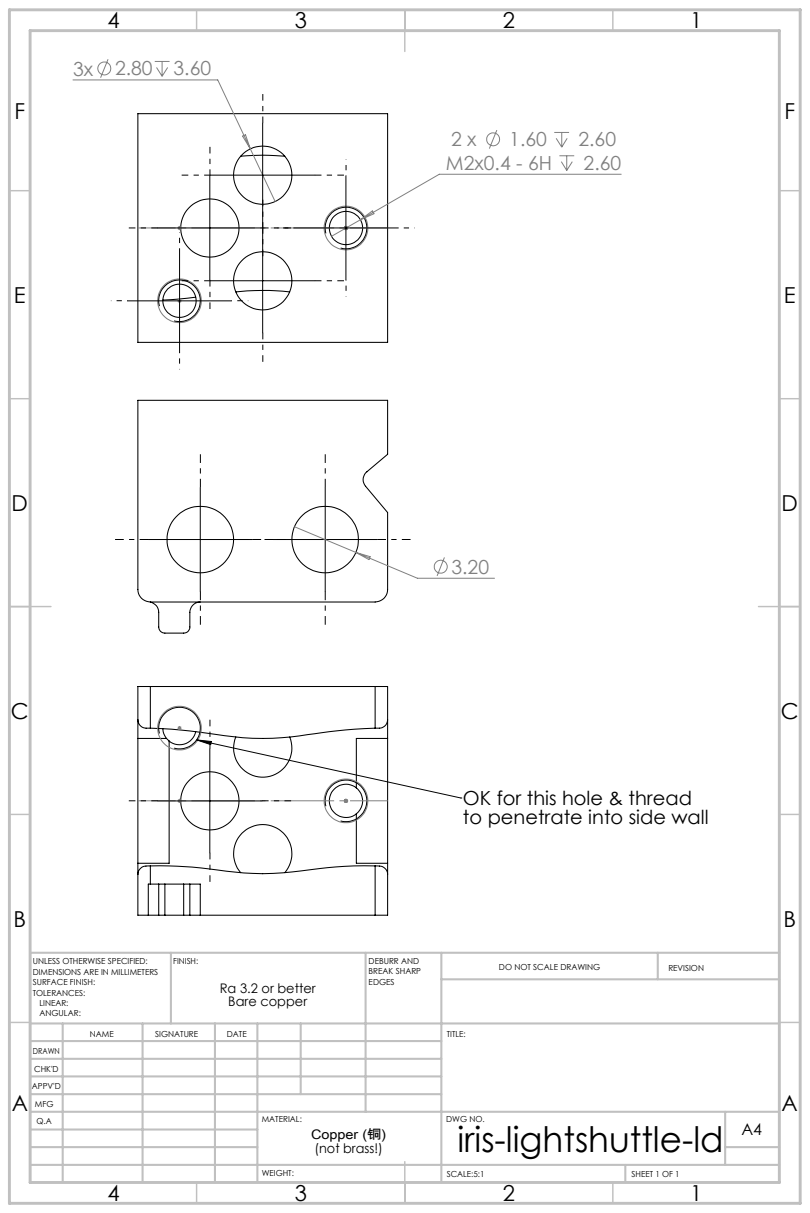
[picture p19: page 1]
FINISH:; DEBURR AND; BREAK SHARP; DO NOT SCALE DRAWING; REVISION; SCALE:5:1; SHEET 1 OF 1

OK for this hole & thread
to penetrate into side wall

UNLESS OTHERWISE SPECIFIED:
DIMENSIONS ARE IN MILLIMETERS
SURFACE FINISH:
TOLERANCES:
LINEAR:
ANGULAR:

Ra 3.2 or better
Bare copper

NAME | SIGNATURE | DATE | | | | TITLE:

DRAWN
CHK'D
APPV'D
MFG
Q.A | | | | MATERIAL: Copper (铜) (not brass!) | DWG NO. iris-lightshuttle-ld | A4

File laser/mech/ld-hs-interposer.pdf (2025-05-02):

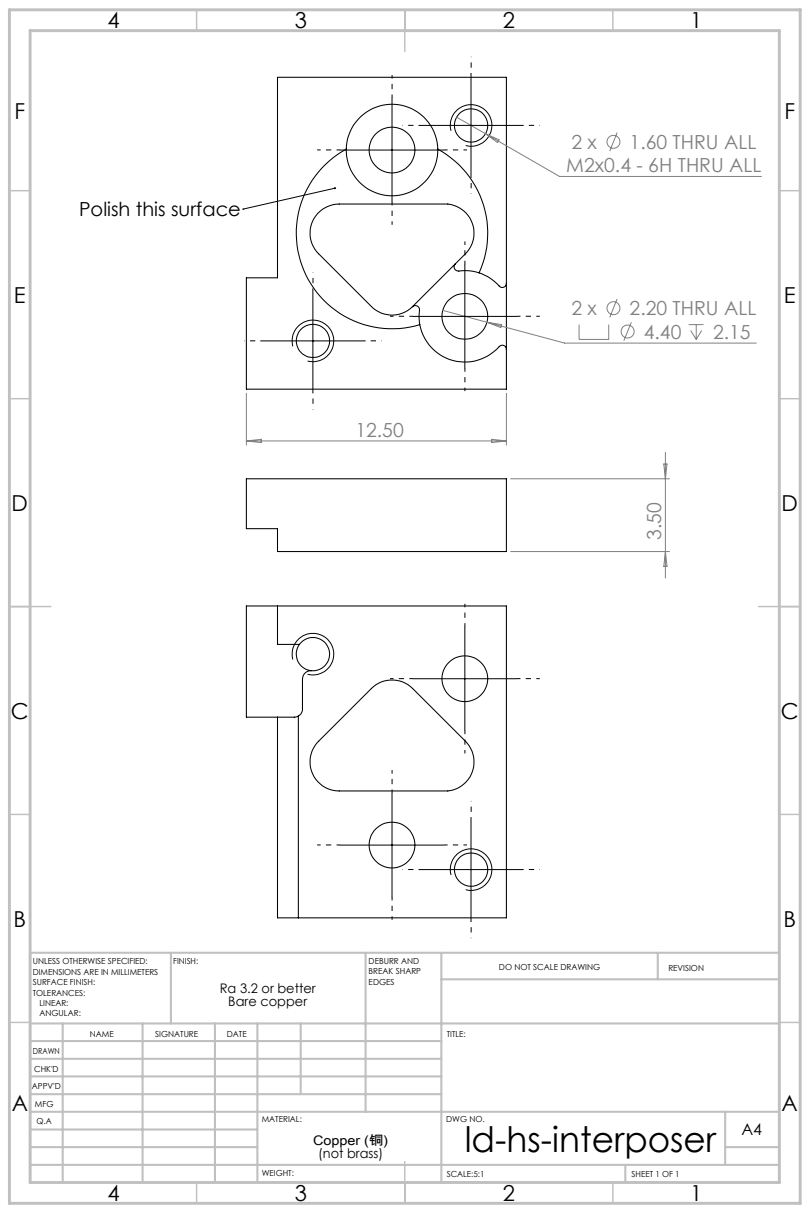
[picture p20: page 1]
1.60 THRU ALL; M2x0.4 - 6H THRU ALL; 2.20 THRU ALL; FINISH:; DEBURR AND; BREAK SHARP; DO NOT SCALE DRAWING; REVISION; SCALE:5:1; SHEET 1 OF 1

Polish this surface

UNLESS OTHERWISE SPECIFIED:
DIMENSIONS ARE IN MILLIMETERS
SURFACE FINISH:
TOLERANCES:
LINEAR:
ANGULAR:

Ra 3.2 or better
Bare copper

NAME | SIGNATURE | DATE | | | | TITLE:

DRAWN
CHK'D
APPV'D
MFG
Q.A | | | | MATERIAL: (not brass) | DWG NO. ld-hs-interposer | A4 Copper (铜)

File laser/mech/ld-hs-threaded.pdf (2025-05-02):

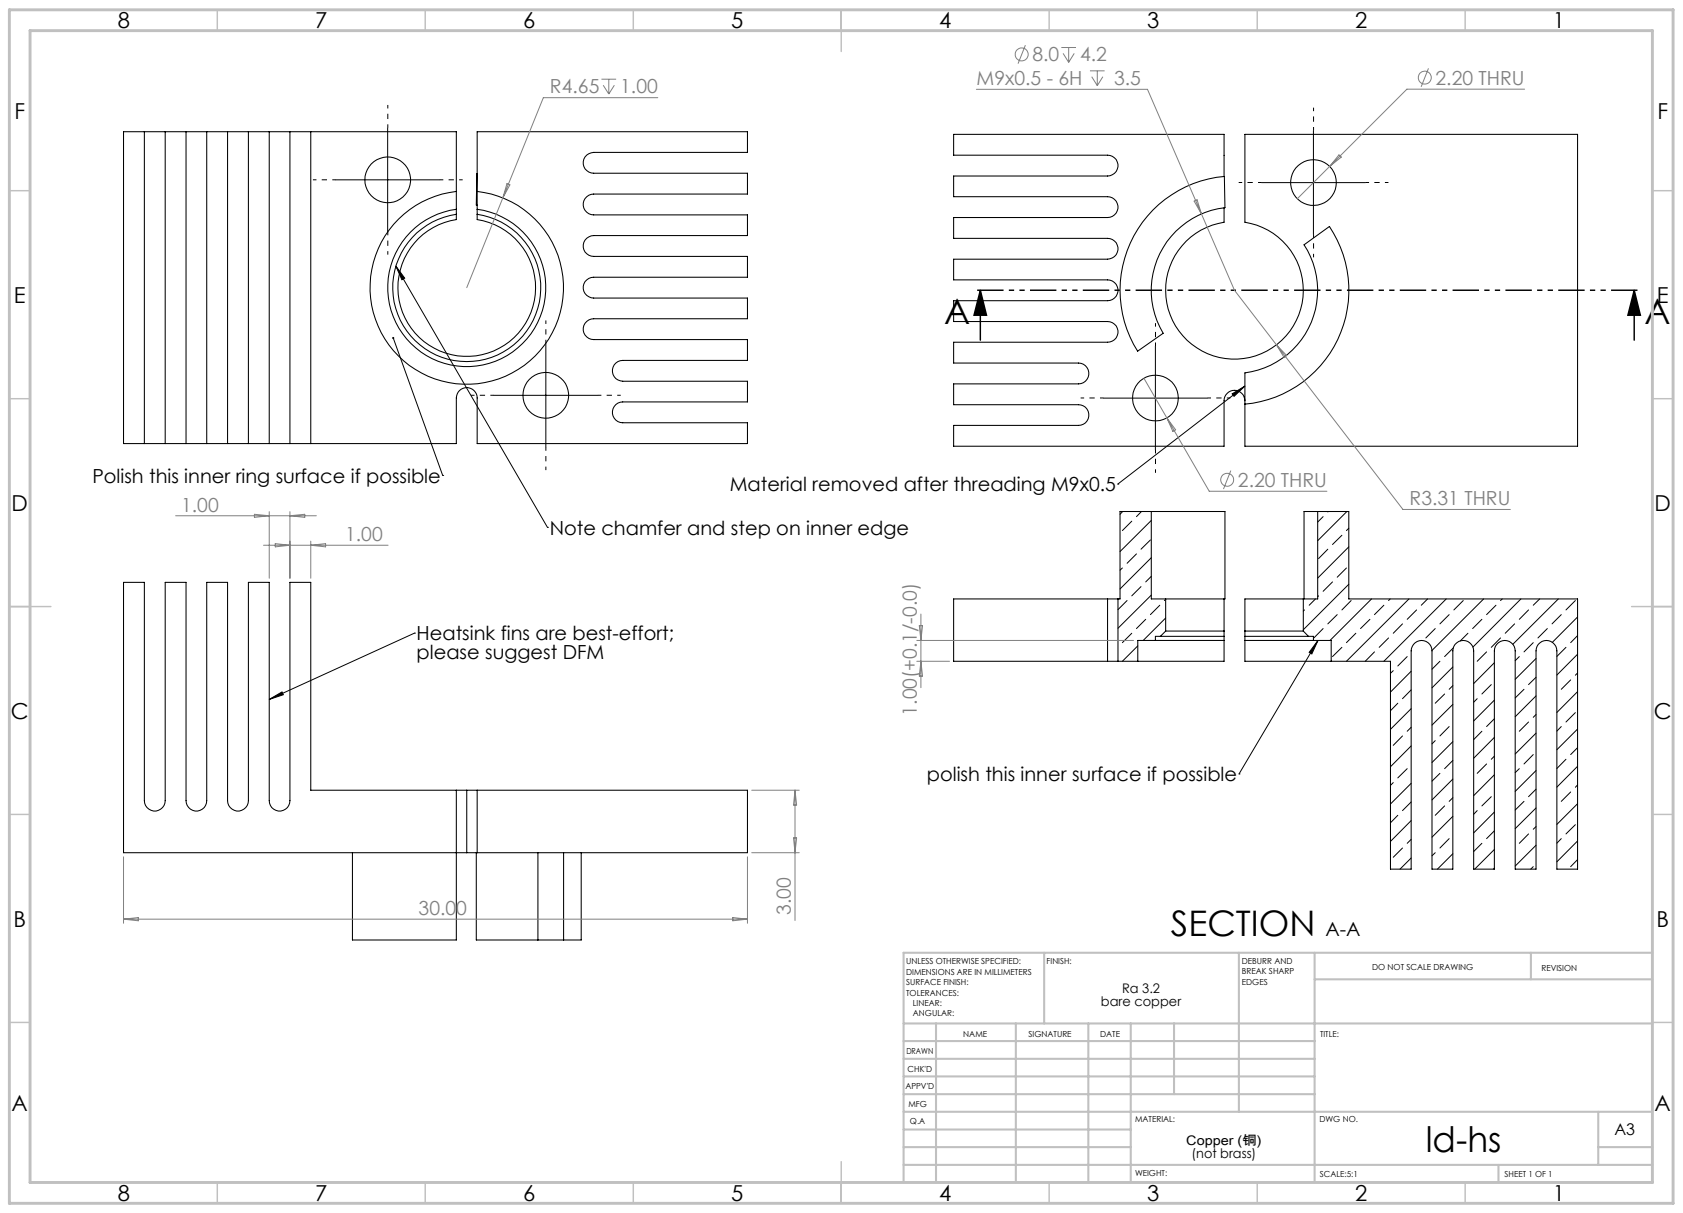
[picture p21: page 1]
2.20 THRU; R3.31 THRU; SECTION A-A; FINISH:; DEBURR AND; BREAK SHARP; DO NOT SCALE DRAWING; REVISION; SCALE:5:1; SHEET 1 OF 1; Ra 3.2 bare copper

8.0 4.2 M9x0.5 - 6H 3.5 | 2.20 THRU

Polish this inner ring surface if possible

Material removed after threading M9x0.5 1.00(+0.1/-0.0)

Note chamfer and step on inner edge

Heatsink fins are best-effort;
please suggest DFM

polish this inner surface if possible

UNLESS OTHERWISE SPECIFIED:
DIMENSIONS ARE IN MILLIMETERS
SURFACE FINISH:
TOLERANCES:
LINEAR:
ANGULAR:

NAME | SIGNATURE | DATE | | | | TITLE:

DRAWN
CHK'D
APPV'D
MFG
Q.A | | | | MATERIAL: (not brass) | DWG NO. ld-hs | A3 Copper (铜)

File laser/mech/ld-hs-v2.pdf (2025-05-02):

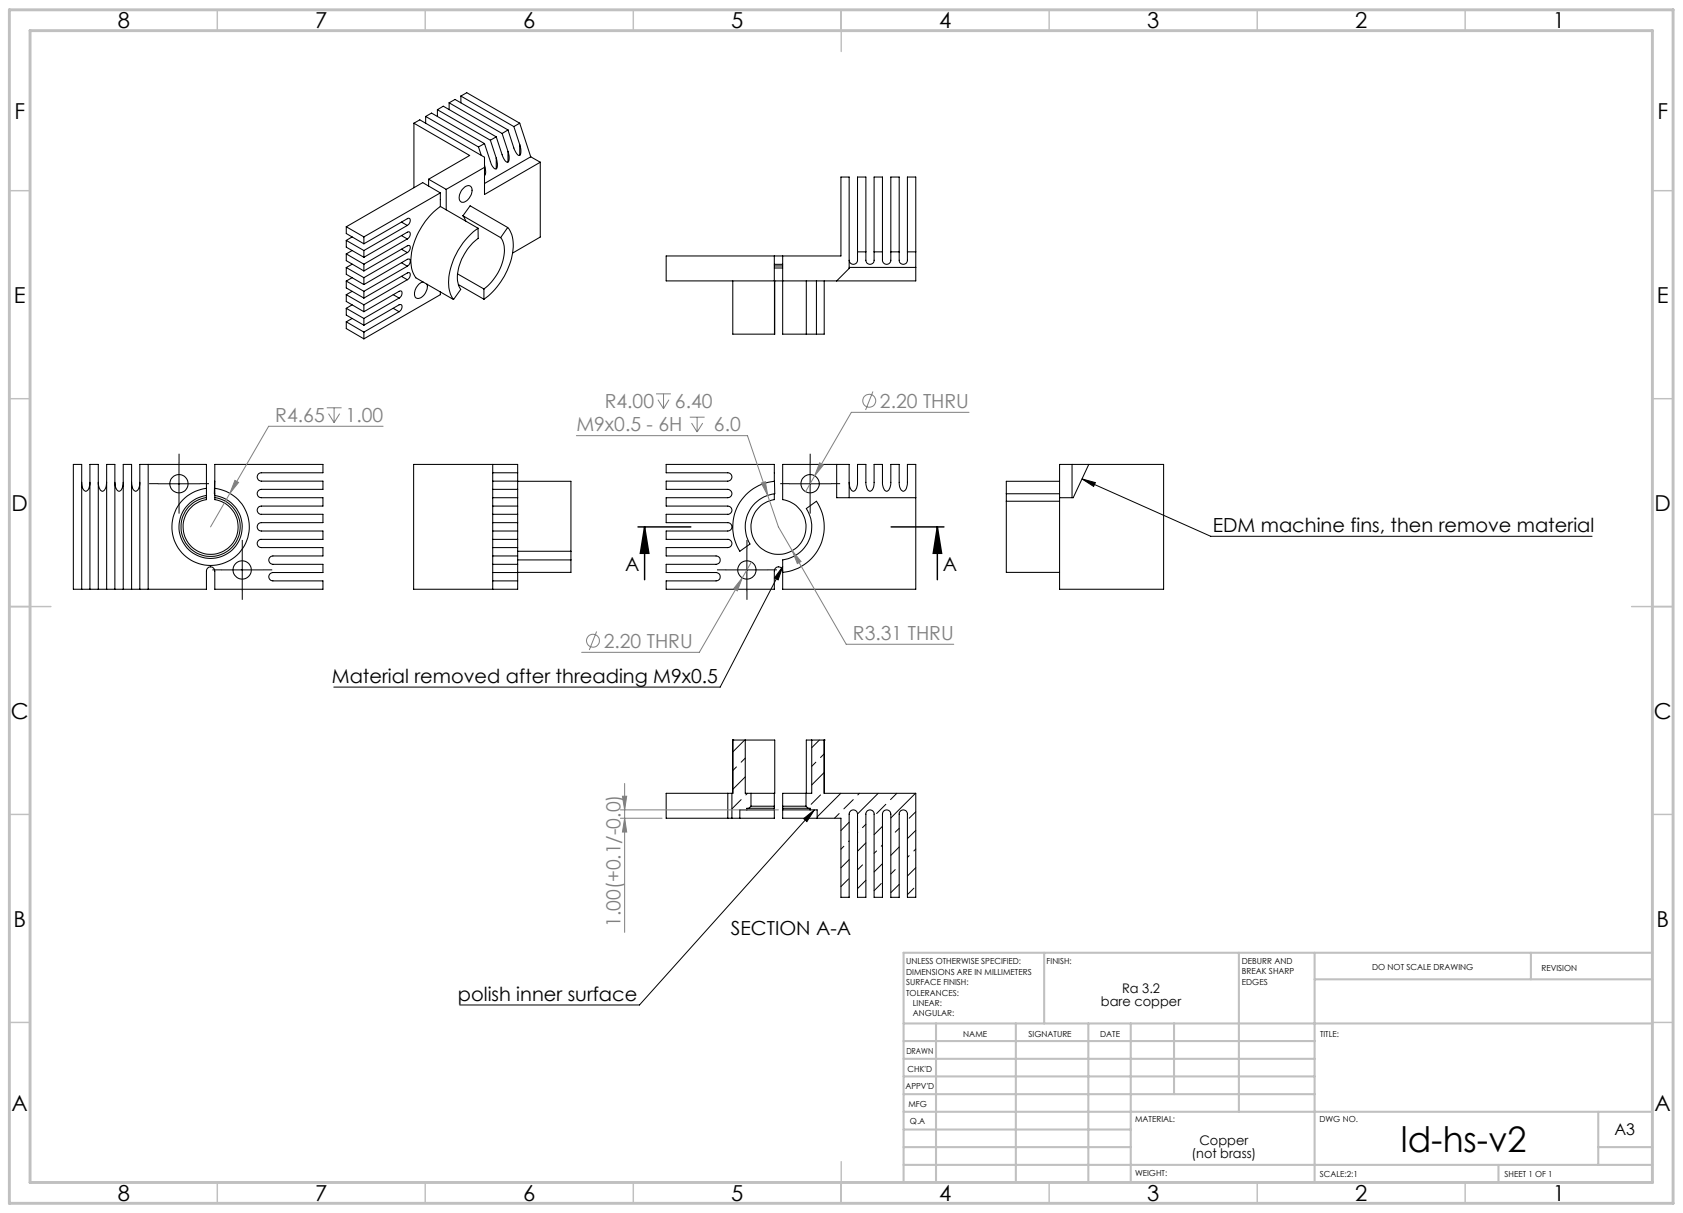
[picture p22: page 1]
2.20 THRU; R3.31 THRU; SECTION A-A; FINISH:; DEBURR AND; BREAK SHARP; DO NOT SCALE DRAWING; REVISION; SCALE:2:1; SHEET 1 OF 1; Ra 3.2 bare copper

EDM machine fins, then remove material

Material removed after threading M9x0.5

UNLESS OTHERWISE SPECIFIED:
DIMENSIONS ARE IN MILLIMETERS
SURFACE FINISH:
TOLERANCES:
LINEAR:
ANGULAR:

polish inner surface

NAME | SIGNATURE | DATE | | | | TITLE:

DRAWN
CHK'D
APPV'D
MFG
Q.A | | | | MATERIAL: (not brass) | DWG NO. ld-hs-v2 | A3 Copper

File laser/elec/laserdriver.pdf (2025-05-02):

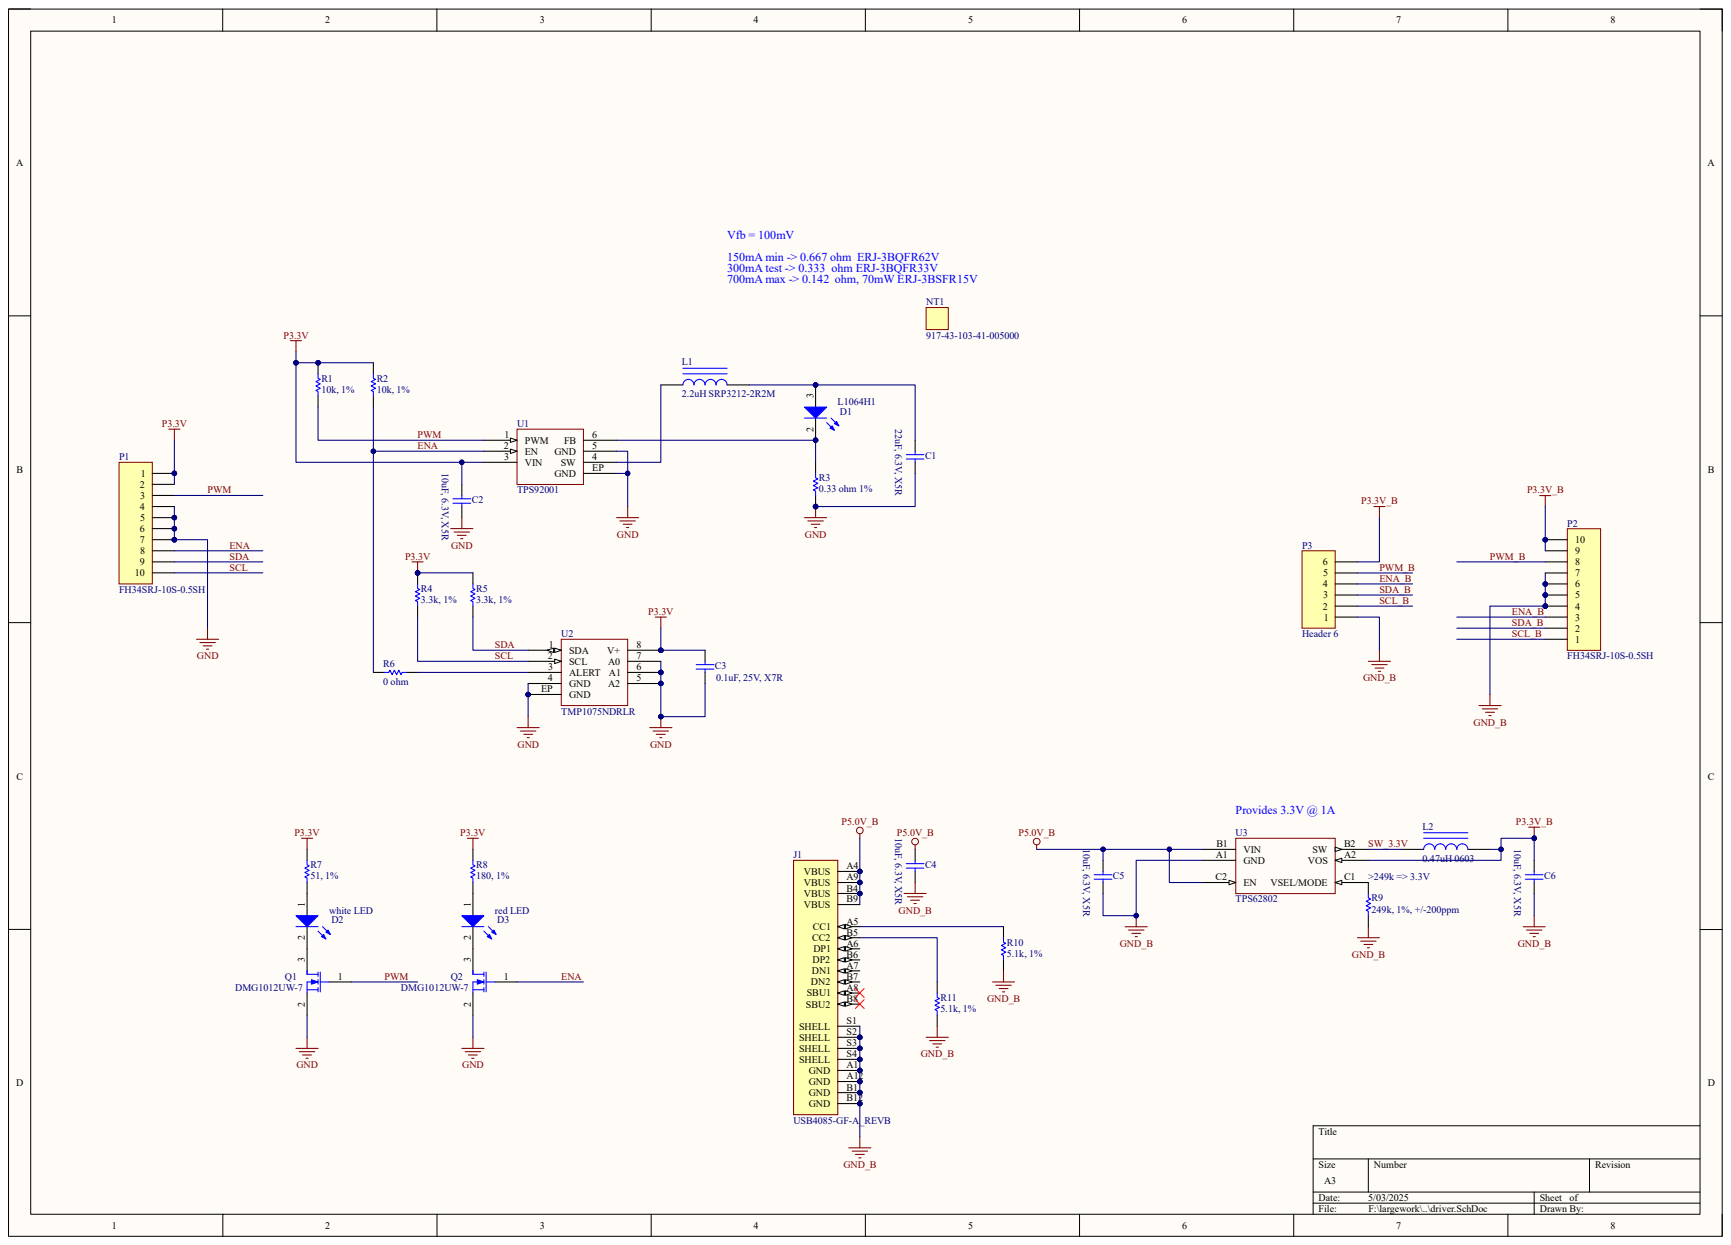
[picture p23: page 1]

Date: 5/03/2025 | Sheet of
File: F:\largework\..\driver.SchDoc | Drawn By:

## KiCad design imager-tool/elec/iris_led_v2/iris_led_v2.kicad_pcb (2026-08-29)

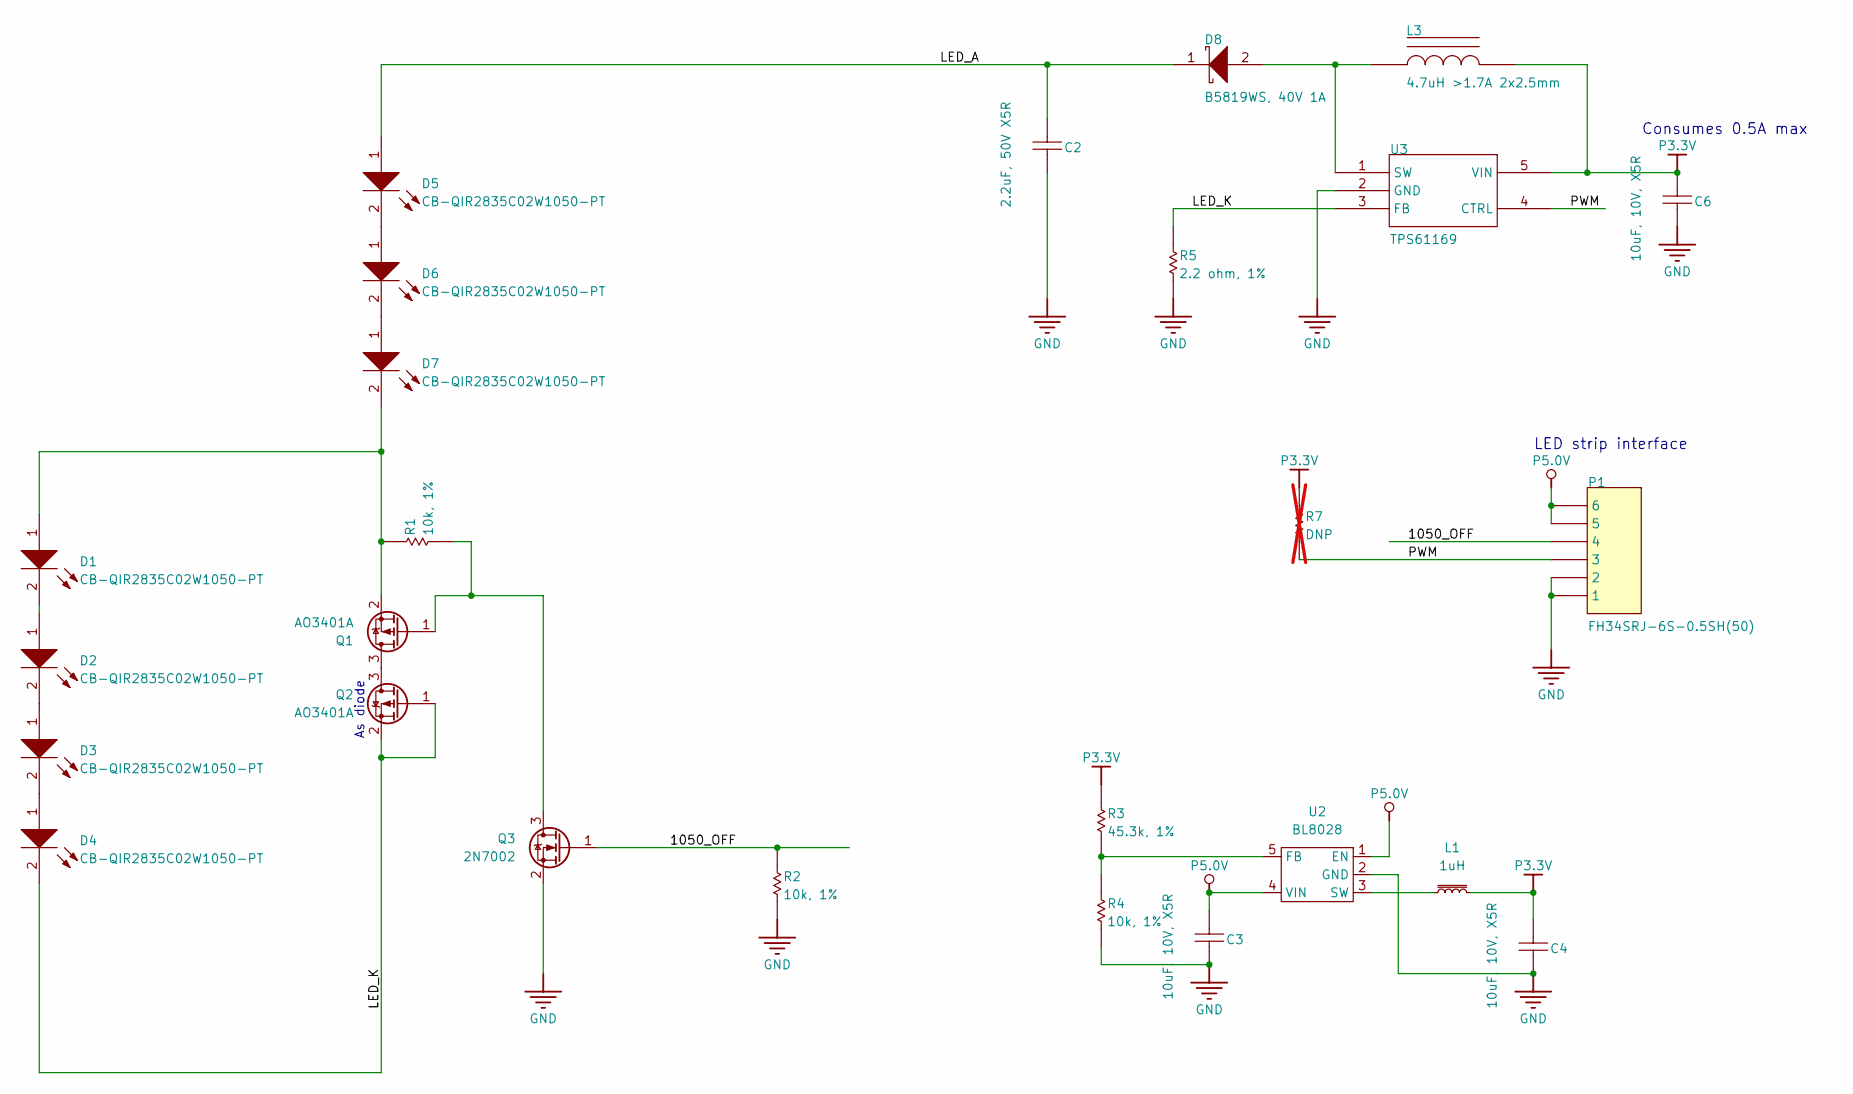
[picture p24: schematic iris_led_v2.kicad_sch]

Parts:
C2: 2.2uF, 50V X5R; C_0805_2012Metric; MPN CL21A225KBQNNNE; JLCPCB C377773
C3, C4, C6: 10uF, 10V, X5R; C_0603_1608Metric; MPN CL10A106KP8NNNC; LCSC C19702
D1, D2, D3, D4, D5, D6, D7: CB-QIR2835C02W1050-PT; LED_PLCC_2835; MPN CB-QIR2835C02W1050-PT
D8: B5819WS, 40V 1A; D_SOD-323; MPN B5819WS; LCSC C7420331
L1: 1uH; L_1008_2520Metric; LCSC C435392
L3: 4.7uH >1.7A 2x2.5mm; L_Changjiang_FNR252010S; MPN FTC252010S4R7MBCA; LCSC C5832360
P1: FH34SRJ-6S-0.5SH(50); HRS_FH34SRJ-6S-0.5SH(50); MPN FH34SRJ-6S-0.5SH(50); LCSC C5213748
Q1, Q2: AO3401A; SOT-23
Q3: 2N7002; SOT-23; LCSC C8545
R1, R2, R4: 10k, 1%; R_0402_1005Metric; MPN ANY; LCSC C25744
R3: 45.3k, 1%; R_0402_1005Metric; MPN ANY; LCSC C137977
R5: 2.2 ohm, 1%; R_0603_1608Metric; MPN RC0603FR-7W2R2L; LCSC C22939
R7: DNP; R_0402_1005Metric; MPN DNP; not fitted
U2: BL8028; SOT-23-5; LCSC C266177
U3: TPS61169; SOT-353_SC-70-5; MPN TPS61169DCKR; LCSC C71045

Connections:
/1050_OFF: P1.4, Q3.1 (G), R2.2
/LED_A: C2.1, D5.1 (A), D8.1 (K)
/LED_K: D4.2 (K), Q2.1 (G), Q2.2 (S), R5.1, U3.3 (FB)
/PWM: P1.3, R7.2, U3.4 (CTRL)
GND: C2.2, C3.2, C4.2, C6.2, P1.1, P1.2, Q3.2 (S), R2.1, R4.1, R5.2, U2.2 (GND), U3.2 (GND)
unnamed: D1.1 (A), D7.2 (K), Q1.2 (S), R1.2
unnamed: D1.2 (K), D2.1 (A)
unnamed: D2.2 (K), D3.1 (A)
unnamed: D3.2 (K), D4.1 (A)
unnamed: D5.2 (K), D6.1 (A)
unnamed: D6.2 (K), D7.1 (A)
unnamed: D8.2 (A), L3.1, U3.1 (SW)
unnamed: Q1.3 (D), Q2.3 (D)
unnamed: Q1.1 (G), Q3.3 (D), R1.1
unnamed: R3.1, R4.2, U2.5 (FB)
unnamed: L1.1, U2.3 (SW)
P3.3V: C4.1, C6.1, L1.2, L3.2, R3.2, R7.1, U3.5 (VIN)
P5.0V: C3.1, P1.5, P1.6, U2.1 (EN), U2.4 (VIN)

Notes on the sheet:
Consumes 0.5A max
As diode
LED strip interface

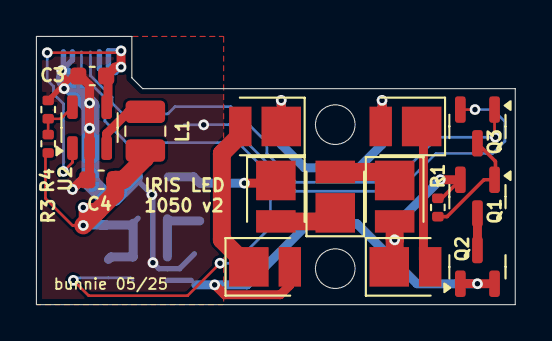
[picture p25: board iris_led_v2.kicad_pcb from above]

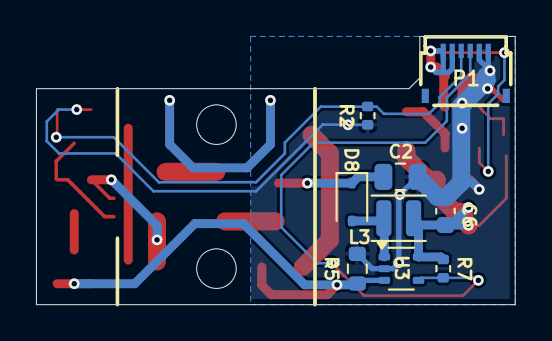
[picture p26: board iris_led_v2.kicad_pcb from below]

Board: 2 copper layers, 26.6 x 14.9 mm, 26 parts (9 on the bottom side), 18 nets.

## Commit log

2024-03-04 add piezo stage files
    [Bill of Materials-piezo-driver1.xlsx, controller.SchDoc, driver.SchDoc, piezo-driver1.PcbDoc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]
2024-03-04 add more iris design files
    [IQ2306 6mm adapter v2.STEP, M3_countersunk_washer_OOTDTY.STEP, iris-actuator-base-plate.SLDDRW, iris-alignment-bracket.SLDDRW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]
2024-03-04 add remaining design files
    [Bill of Materials-led-controller2.xlsx, Bill of Materials-scope-hub.xlsx, Bill of Materials-switches.xlsx, Pick Place for led-controller2.csv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]
2025-05-02 exploration & prototyping of alternate mountings
    A square mounting plate makes it easier to align samples
    to the IRIS system.
    Two variants are included here
    - "square" is designated for direct chip mounts, for generating
    reference images
    - "qsuare-1d" is designated for system-level mounts. it also
    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
    [piezo-top-plate-square-1d.STEP, piezo-top-plate-square.STEP]
2025-05-02 add laser driver and mount
    [Bill of Materials-laserdriver1.xlsx, connecting-rod.STL, driver.SchDoc, hinge.STL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]
2025-05-02 add readme for laser
